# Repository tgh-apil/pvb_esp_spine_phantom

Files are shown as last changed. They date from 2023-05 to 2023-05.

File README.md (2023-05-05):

# APIL PVB/ESP Spine Phantom

**NOTE:** This is a **highly** experimental phantom.  Due to the number of individual muscle layers, size of each layer, and complexity of layer fusion, this phantom has a very low yield.  We are currently in the process of updating and experimenting further with this phantom.

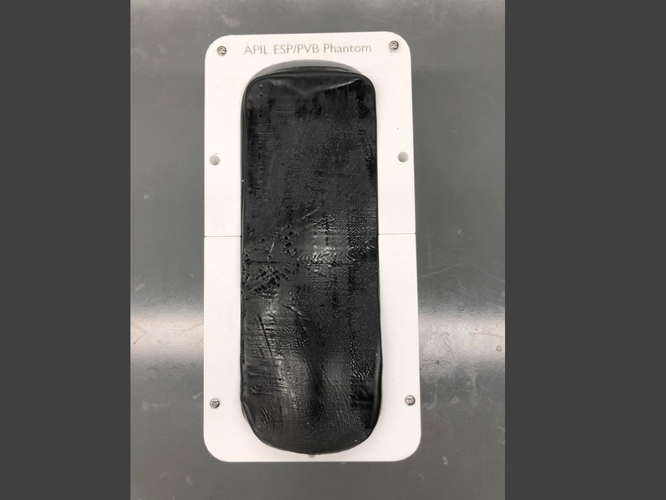
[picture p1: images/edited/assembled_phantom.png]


3D Printed mid-thoracic (T6 - L2) spine based on CT data.  Our spine phantom is encased in an synthetic, shelf-stable gel which has a realistic tactile feel to human muscle and is echogenic.  This phantom contains individual muscle layers to simulate the trapezius, rhomboid, and erector spinae muscles.  These layers are distinct which and which allows a bolus of fluid to be deposited between any of the layers.  A bolus of fluid can also be deposited underneath the transverse process to simulate entering the potential space of the PVB technique.

This model was developed at the [Lynn & Arnold Irwin Advanced Perioperative Imaging Lab](https://apil.ca), Toronto General Hospital, University Health Network.

# Purchasing Information
To purchase this phantom, please email <apil@uhn.ca> and a represtative will be in touch with you with more details.

**A purchased phantom contains the following**:

1. Fully assembled scoliotic spine phantom.
2. Custom table clamp to hold phantom to tabe surface

# Ultrasound Images
Coming soon

# Care and Maintenance
1. Apply generous amount of ultrasound gel to surface of phantom.
2. When attempting the PVB technique, the fluid will collect in the 3D printed case automatically.  Please empty the collected fluid after every use.

# Materials & Equipment

## Hardware

- M5*14 pins
- 2 x M4*16 Bolts
- 4 x M4*20 Bolts
- Heat gun
- Super glue

## Printing Equipment

- Polylactic Acid (PLA)
- High temperature PLA (htPLA)
- Bridge Nylon
- Fused Deposition Modelling 3D printer

## Casting Equipment

- Ballistics Gel
  - Gelatin #3 from [Humimic Medical](https://humimic.com/product/gelatin-3-medical-gel-by-the-pound/)
- Graphite Powder (optional)
  - used to replicate echogenic scatter of muscle
- Slowcooker
- Two-part Platinum Cure Silicone Rubber (or equivalent)
  - Available from [Smooth-On](https://www.smooth-on.com/products/dragon-skin-30/)
- Degas Chamber (Optional)

# Assembly Instructions

## Printing

This repo includes **stl** files for each printed part.

In general, we use the following settings for *all* parts of this phantom:

<table>
    <tr>
        <td><b>Material</b></td>
        <td><b>Colour</b></td>
        <td><b>Nozzle Temp (C)</b></td>
        <td><b>Bed Temp (C)</b></td>
        <td><b>Infill (%)</b></td>
        <td><b>Perimiters (#)</b></td>
    </tr>
    <tr>
        <td>PLA</td>
        <td>White</td>
        <td>210.0</td>
        <td>60.0</td>
        <td>10.0</td>
        <td>2</td>
    </tr>
    <tr>
        <td>htPLA</td>
        <td>White</td>
        <td>210.0</td>
        <td>60.0</td>
        <td>10.0</td>
        <td>2</td>
    </tr>
    <tr>
        <td>Bridge Nylon</td>
        <td>Natural</td>
        <td>250.0</td>
        <td>80.0</td>
        <td>15.0</td>
        <td>3</td>
    </tr>
</table>

## Silicone Casting

### Silicone Mold Casting

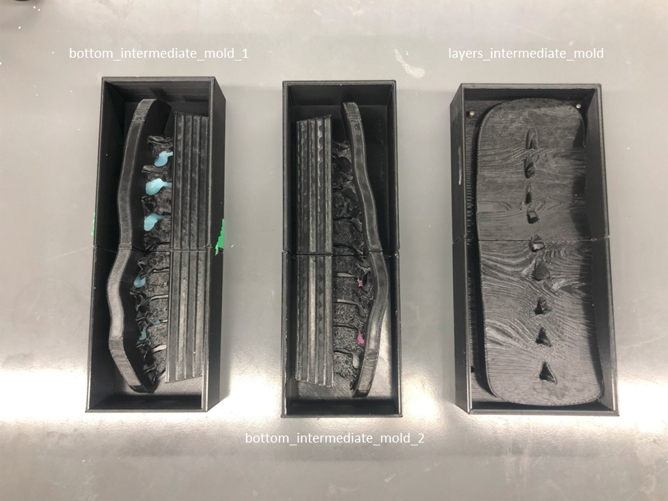
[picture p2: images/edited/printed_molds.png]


1. Print all components in the directory */molds/* using the PLA printing settings outlined above.
2. Assemble bottom_intermediate_mold_1a, 1b and bottom_intermediate_mold_2a, 2btogether using M5*14 pins.
3. Assemble layers_intermediate_mold_1 and 2 together using M5*14 pins.
4. Mix **3000 g** of silicone according to manufacturers instructions.
    - Degassing the silicone is encoraged, but optional.
    - Adding colourant to silicone is optional.
5. Pour silicone into the assembled molds until flush with top surface.
6. Allow silicone to cure according to manufacturer's instructions.
7. Carefully disassmble the mold and release the silicone.
   - **NOTE:** This step can be very difficult.  Procede with caution and patience to avoid damaging the silicone shell.

## 3D Printing Components

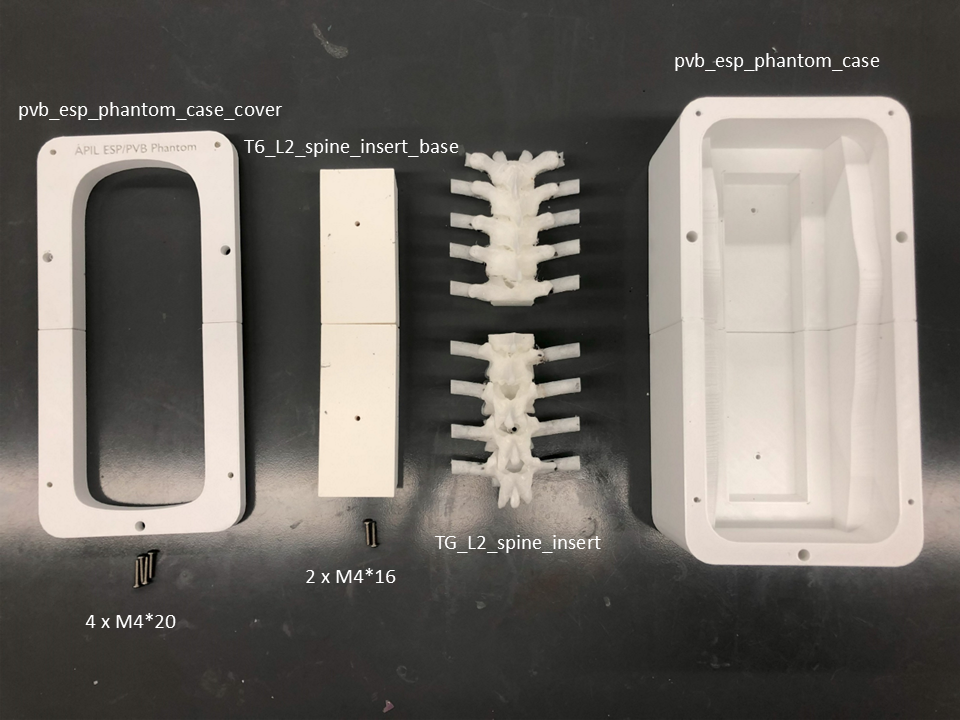
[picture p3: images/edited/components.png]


1. Print all components in the directory */insert/* 
   1. Use Bridge printing settings for T6_L2_spine_insert_1 and 2.
   2. Use htPLA printing settings for T6_L2_spine_insert_base_1 and 2. 
2. Print all components in the directory */case/* using the PLA printing settings outlined above.
3. Carefully remove supports from the part when complete.
   1. You can leave the supports underneath the spinous processes.
4. Assemble the printed base with 2 x M5*14 pins
5. Assemble the two spine halves to the base with 2 x M4*16
   1. the spine halves can rotate -- this is a design choice to make it easier to position inside the molds in the next step.
6. Assemble pvb_esp_phantom_case_1 and 2 with 2 x M5*14 pins and super glue.
7. Assemble pvb_esp_pahantom_case_cover_1 and 2 with 2 x M5*14 pins and super glue.

## Ballistics Gel Casting

1. **CAUTION:** Use appropriate heat-proof gloves when working with liquefied ballistic gel and/or heat gun.
2. **CAUTION:** work **only** in a very well ventilated area.  A fumehood is *highly* recommended.

### Ballistics Gel Casting

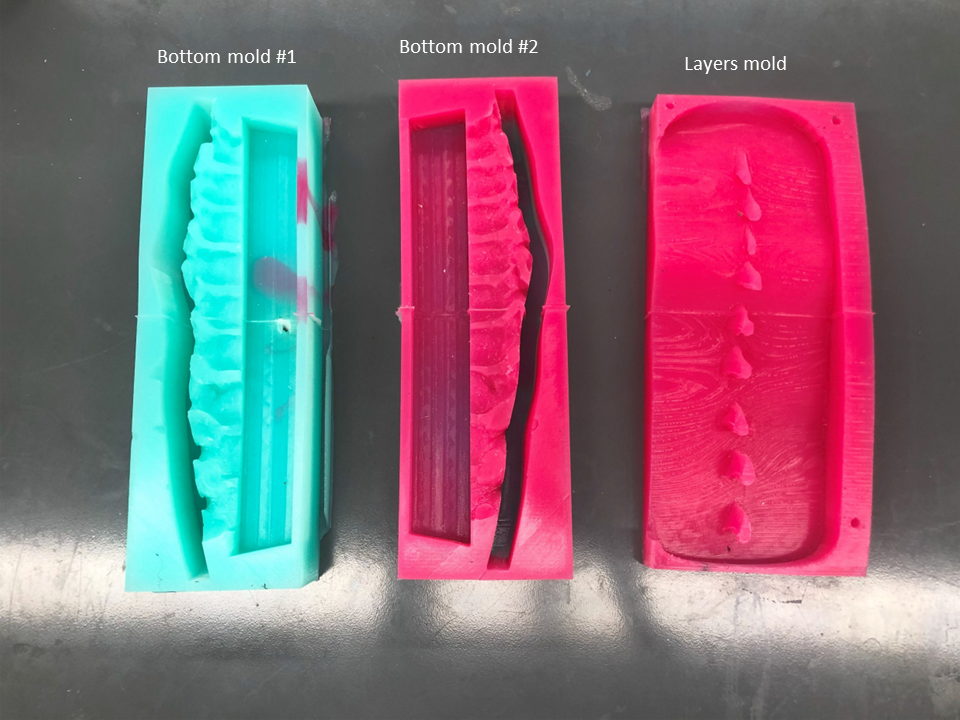
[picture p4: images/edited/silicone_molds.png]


1. Melt at least **1500 g** gel in crockpot @ 105C - 115C (approx. 225F - 240F).
2. If the gel does not contain graphite powder, slowly add graphite powder into fully liquefied mixture until saturated.
3. Once the gel is fully liquefied, pour into one of the bottom silicone molds until gel is flush with the top of the mold.
4. Insert the assembled spine insert into the bottom silicone mold.
5. Allow gel to cool and repeat for second bottom silicone mold.
6. Pour gel into the layers mold until surface is smooth and flat
7. Allow gel to cool and remove from mold.  This is the first muscle layer for the PVB/ESP phantom.
8. Apply the heat gun set to 400C to the underside of the resulting muscle layer.  Move the heat gun evenly accross the surface until it is smooth.
   1. It is crtiical that both sides of the muscle layers are smooth and free of defects otherwise the ultrasound signal may be occluded.
   2. It is critical that that the heat gun be moving constantly or you risk deforming the surface.  The geometry of the muscle is critical to having adequate contact between the gel layers for adequate imaging.
9.  repeat steps 6 -> 8 two more times to produce a total of 3 muscle layers (trapezius, rhomboid, and erector spinae muscles)
10. layer each muscle on to the assembled spine insert.

## Gel Layer Fusion

1. Apply the heat gun set to 400C around the perimeter of the gel layers.
2. Constantly move the heat gun to prevent over-melting of layers.
3. the goal is to fuse the outermost surface of the gel layers **only**.
4. Allow gels to cool completely.  

## Phantom Assembly

1. Place assembled spine insert with gel into assembled case.
2. Attach assembled case cover to the case with 4 x M4*20 bolts.

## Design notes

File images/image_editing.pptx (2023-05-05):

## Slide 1

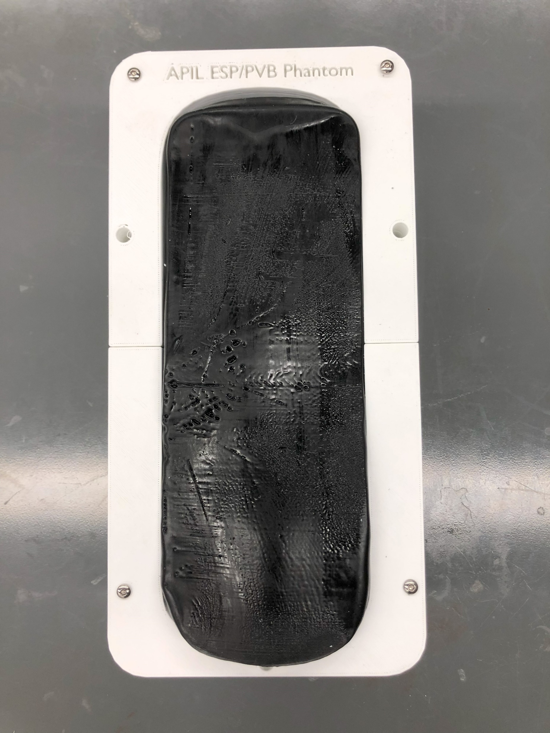
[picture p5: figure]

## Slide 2

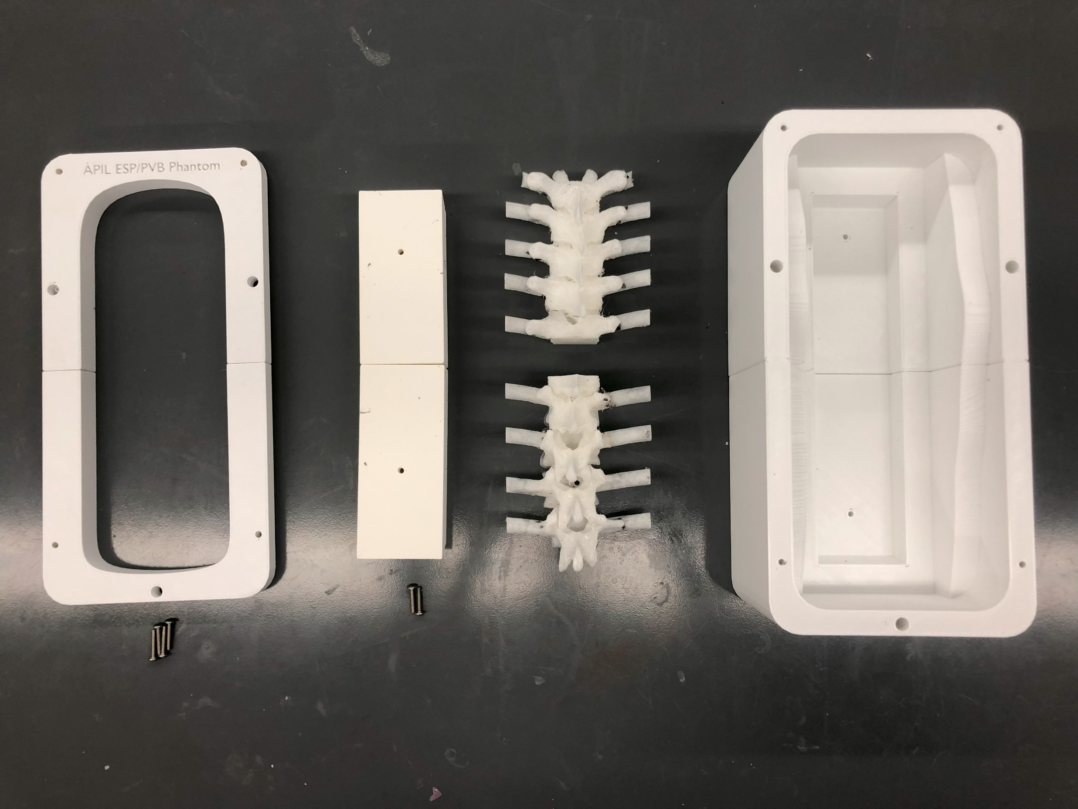
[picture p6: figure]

pvb_esp_phantom_case

pvb_esp_phantom_case_cover

T6_L2_spine_insert_base

TG_L2_spine_insert

2 x M4*16

4 x M4*20

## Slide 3

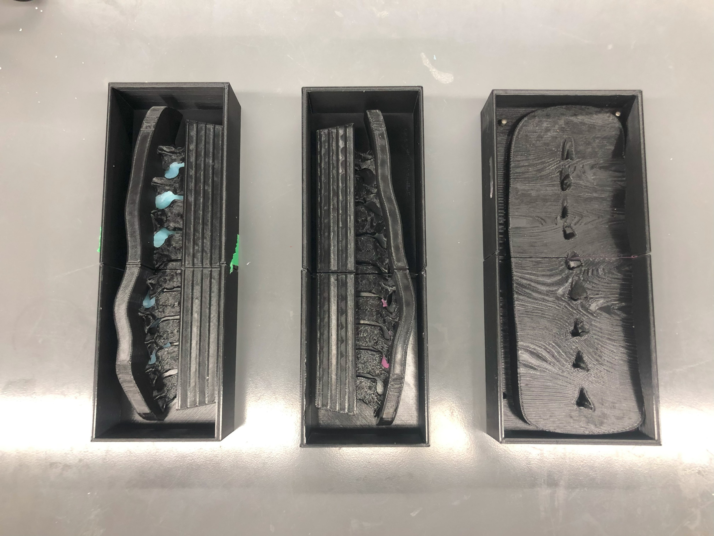
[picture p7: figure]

bottom_intermediate_mold_1

layers_intermediate_mold

bottom_intermediate_mold_2

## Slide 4

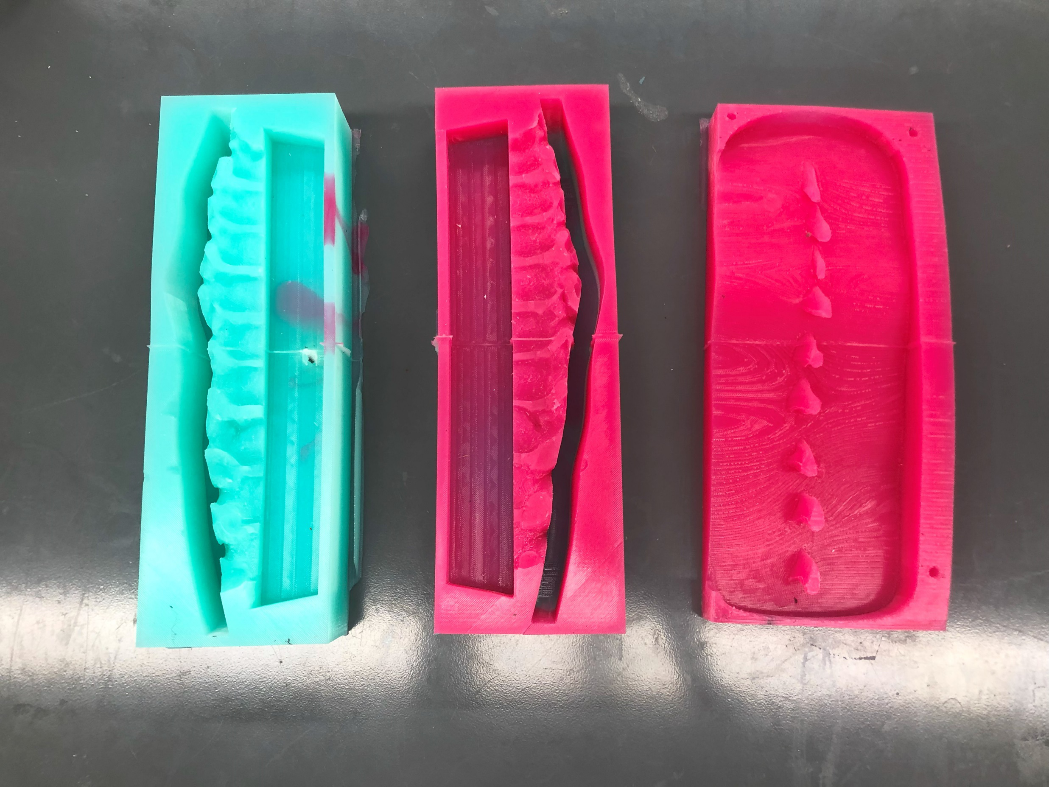
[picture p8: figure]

Bottom mold #1

Bottom mold #2

Layers mold

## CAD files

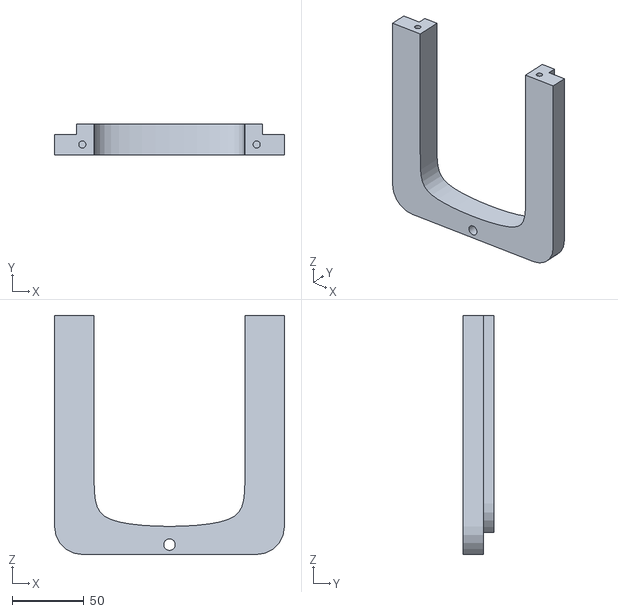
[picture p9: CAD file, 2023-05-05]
case/pvb_esp_phantom_case_cover_2.stl
160.0 x 21.4 x 166.3

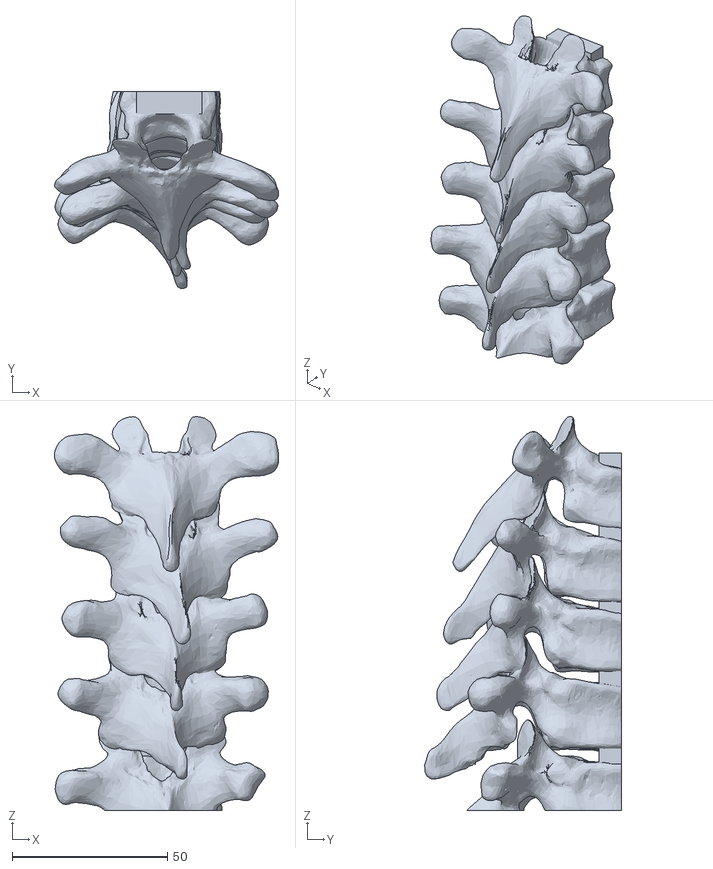
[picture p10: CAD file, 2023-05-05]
insert/T6_L2_spine_insert_1.stl
72.2 x 63.4 x 126.9

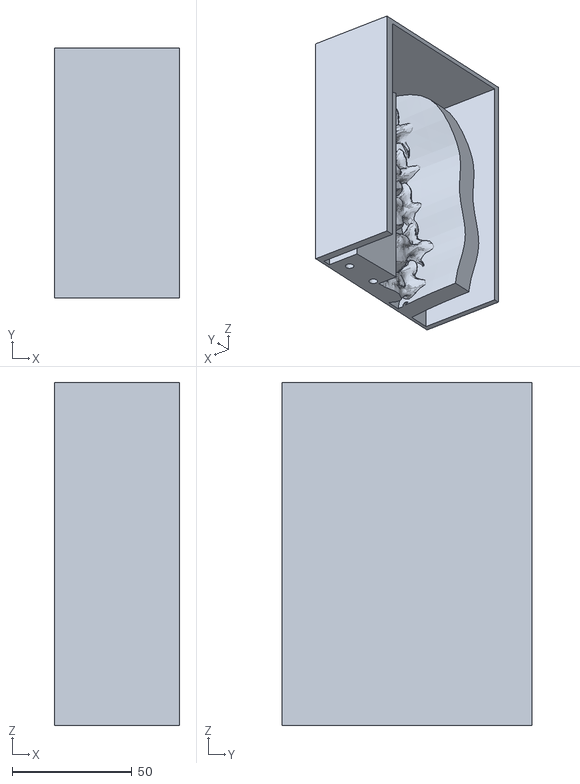
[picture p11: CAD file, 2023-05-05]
molds/bottom_intermediate_mold_2a.stl
52.2 x 104.5 x 143.3

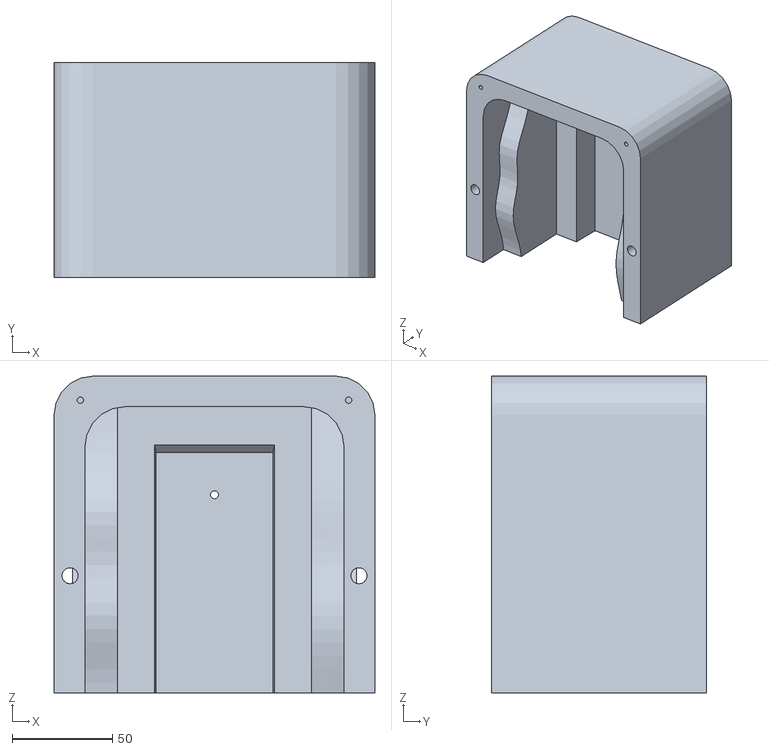
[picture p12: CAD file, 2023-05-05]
case/pvb_esp_phantom_case_1.stl
160.0 x 107.1 x 157.9

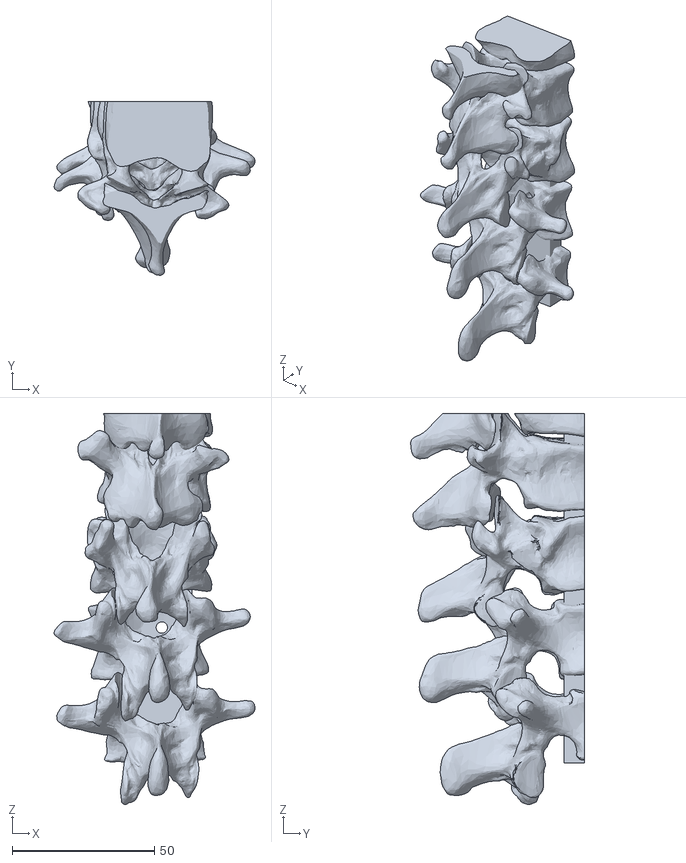
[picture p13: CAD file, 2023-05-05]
insert/T6_L2_spine_insert_2.stl
70.7 x 61.1 x 137.5

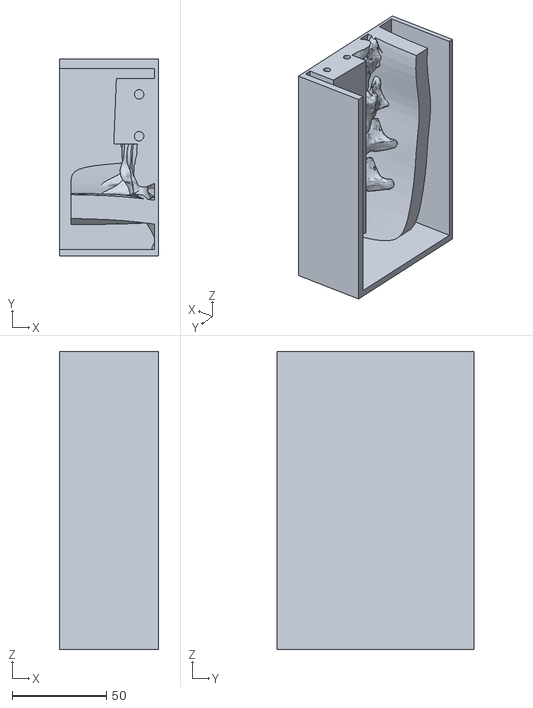
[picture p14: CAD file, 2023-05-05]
molds/bottom_intermediate_mold_2b.stl
52.2 x 104.5 x 157.7

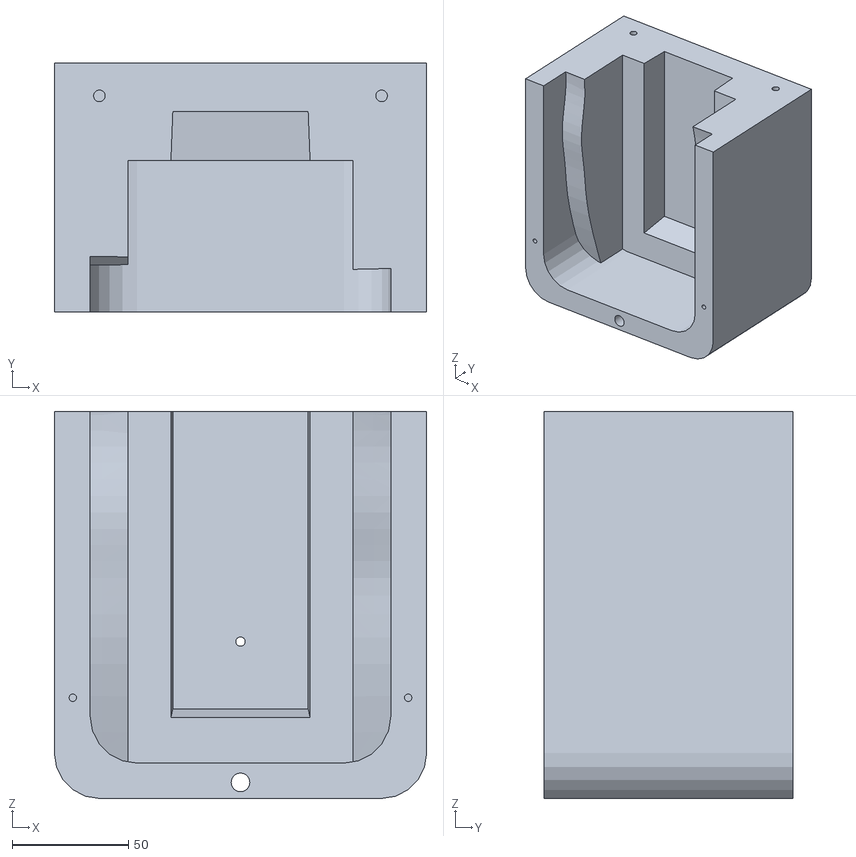
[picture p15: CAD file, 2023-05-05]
case/pvb_esp_phantom_case_2.stl
160.0 x 107.1 x 166.3

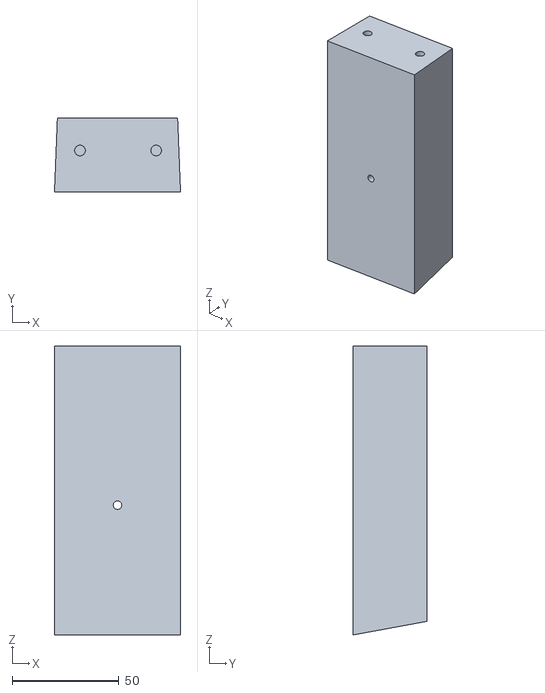
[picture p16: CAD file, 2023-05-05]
insert/T6_L2_spine_insert_base_2.stl
59.0 x 34.8 x 135.2

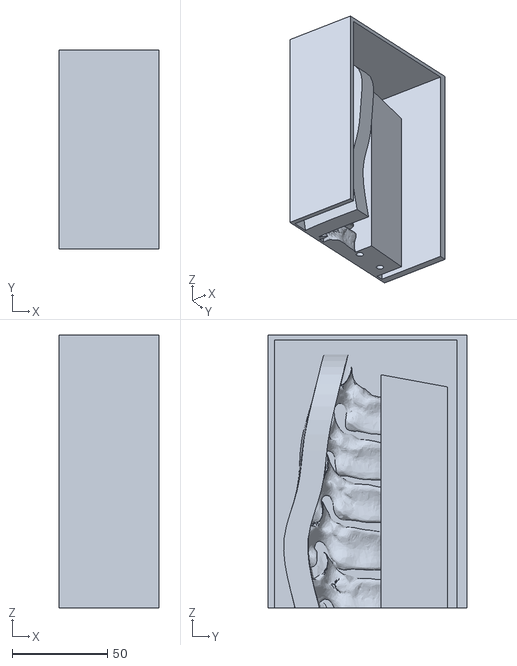
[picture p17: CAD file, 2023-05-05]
molds/bottom_intermediate_mold_1a.stl
52.2 x 104.5 x 143.3

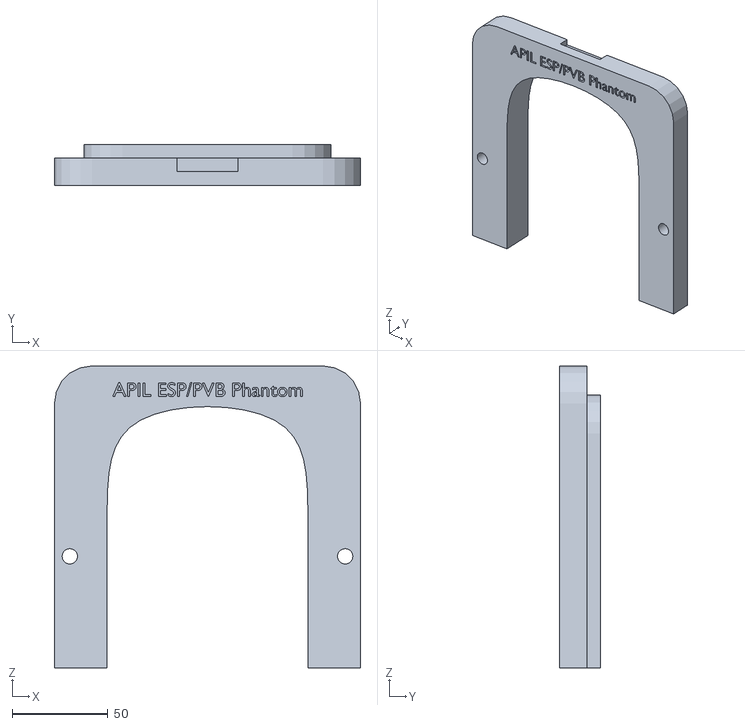
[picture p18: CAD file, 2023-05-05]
case/pvb_esp_phantom_case_cover_1.stl
160.0 x 21.4 x 157.9

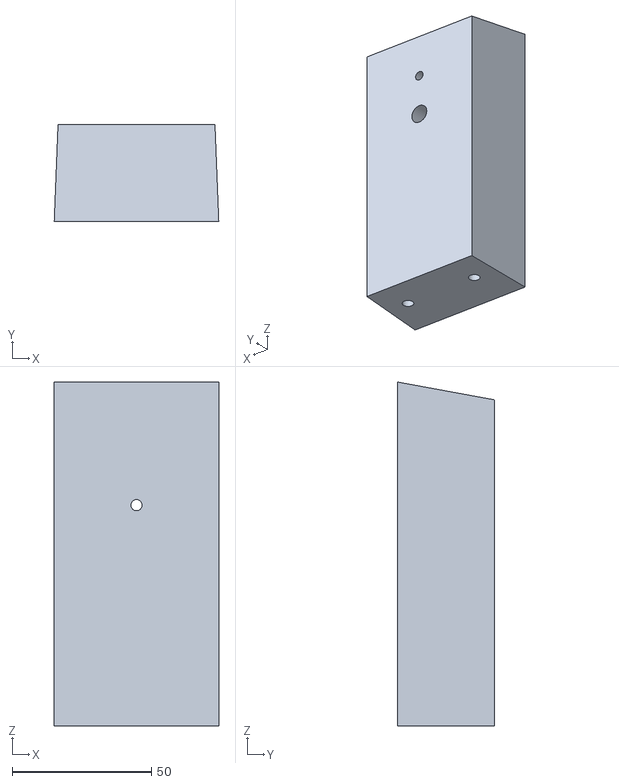
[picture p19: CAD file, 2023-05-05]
insert/T6_L2_spine_insert_base_1.stl
59.0 x 34.8 x 123.3

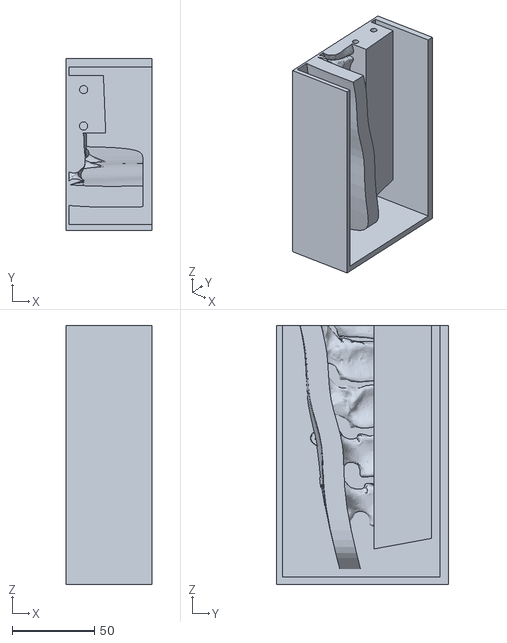
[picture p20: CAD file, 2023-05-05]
molds/bottom_intermediate_mold_1b.stl
52.2 x 104.5 x 157.7

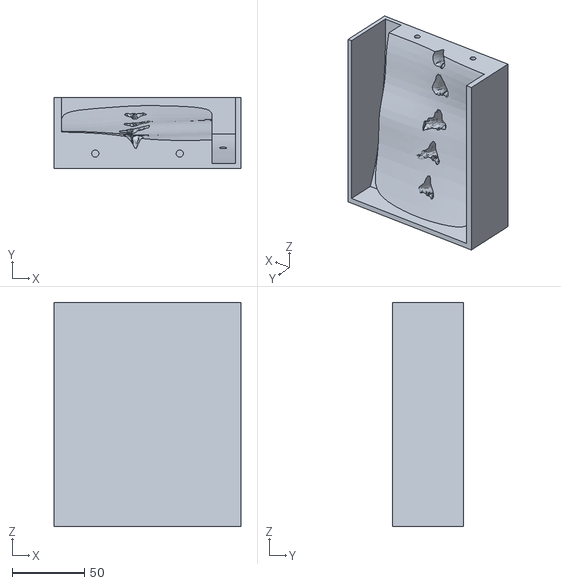
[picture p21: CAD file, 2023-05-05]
molds/layers_intermediate_mold_2.stl
129.3 x 49.0 x 155.0

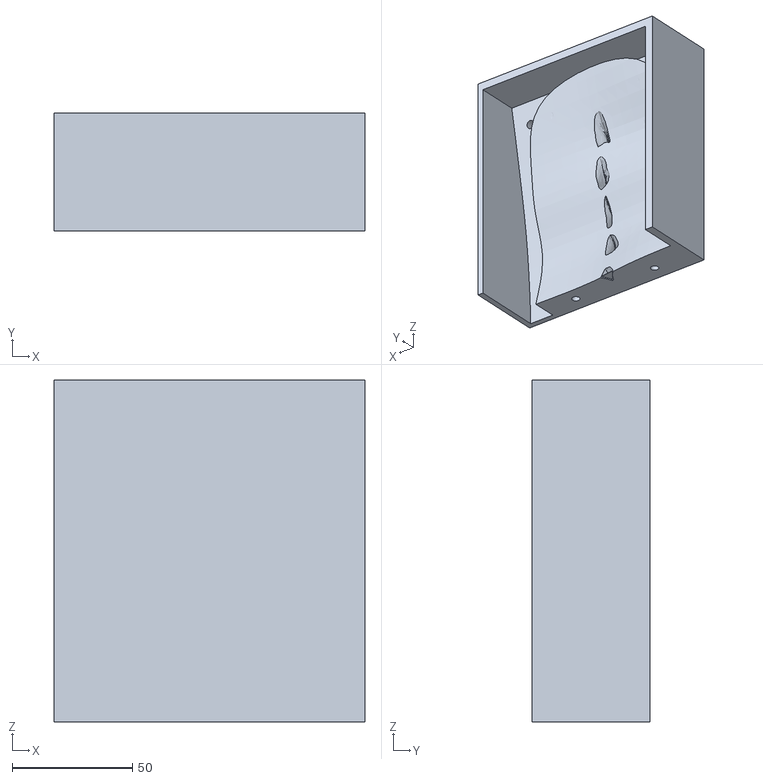
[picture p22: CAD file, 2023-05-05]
molds/layers_intermediate_mold_1.stl
129.3 x 49.0 x 142.3
